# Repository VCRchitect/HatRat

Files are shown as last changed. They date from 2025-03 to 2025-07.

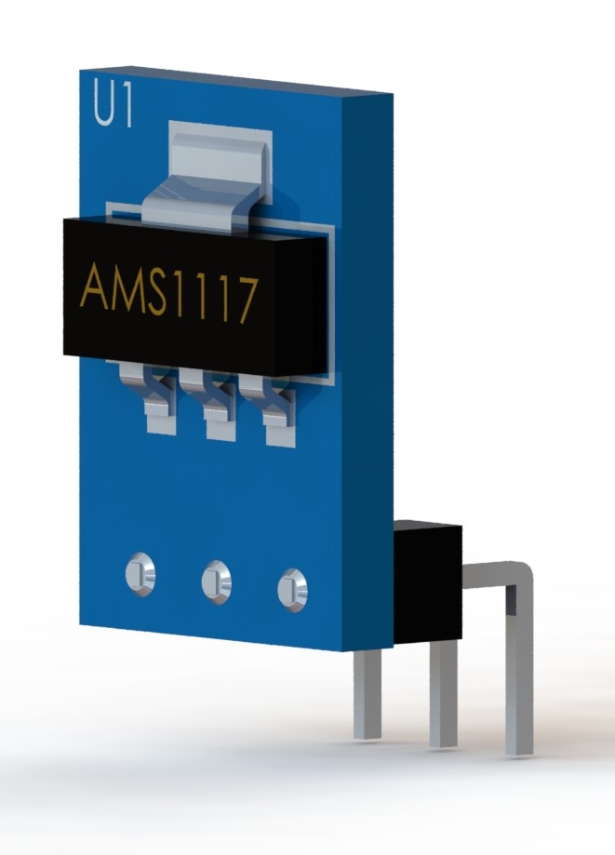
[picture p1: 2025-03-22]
KiCAD Files/Symbols and Resources/3D Models/ams1117-1.snapshot.3/AMS1117.101.jpg

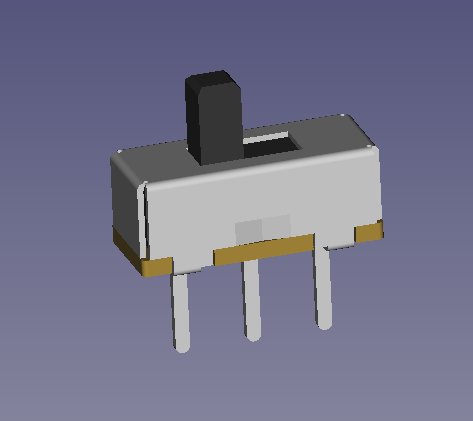
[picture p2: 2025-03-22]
KiCAD Files/Symbols and Resources/3D Models/ss12d00-1.snapshot.10/SS12D00 view 1.jpg

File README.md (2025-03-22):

HatRat, the Mouse For Your Hat!
======

This project is an attempt to make an inexpensive, easy-to-use head mouse. The shell is 3D printed and features a clip to put it on a hat, visor, or maybe even a glasses frame. 

To use the device, clip it onto something with the USB C port facing outward toward the screen. Connect a USB cable and the device will automatically turn on. Move your head up, down, left, or right to move the mouse accordingly. 

How to Use the HatRat
======
If you hold still (or even just relatively still) for 3 seconds, the mouse will enter a gesture mode:
1.  Tilt left then back to center to left-click the mouse.
2.  Tilt right then back to center to right-click the mouse.
3.  To left-click and drag, tilt to the left and keep tilted. Move your head in the direction you want to drag while keeping your head tilted. When you're done, tilt your head back to the center.
4.  To right-click and drag, tilt to the right and keep tilted. Move your head in the direction you want to drag while keeping your head tilted. When you're done, tilt your head back to the center.

If you need to reset the orientation of the mouse, look to the edge of the screen. Like, if your head is too far turned to the left, just turn all the way to the right until you're about where you want "right" to be. The same holds true for up, down, left, and right.

If you're clicking and dragging and need to drop something with precision, hold your head still for the 3 seconds to freeze the mouse in place before you tilt the opposite direction to release the click.

In the repository is the Arduino sketch, 3D print files, and KiCAD files needed to build the thing.

Bill of Materials
======
Other than the circuit board, you will need:
-	1x Arduino Pro Micro USB C
-	1x Bidirectional Logic Level Converter
-	1x AMS1117-3.3V Voltage Regulator
-	1x MPU6050 Accelerometer
-	2x Female Headers - 12 Pins - 2.54mm Pitch

You should be able to print the thing with about 25g of filament, making the entire thing cost about $15, versus the hundreds of dollars that other solutions cost.

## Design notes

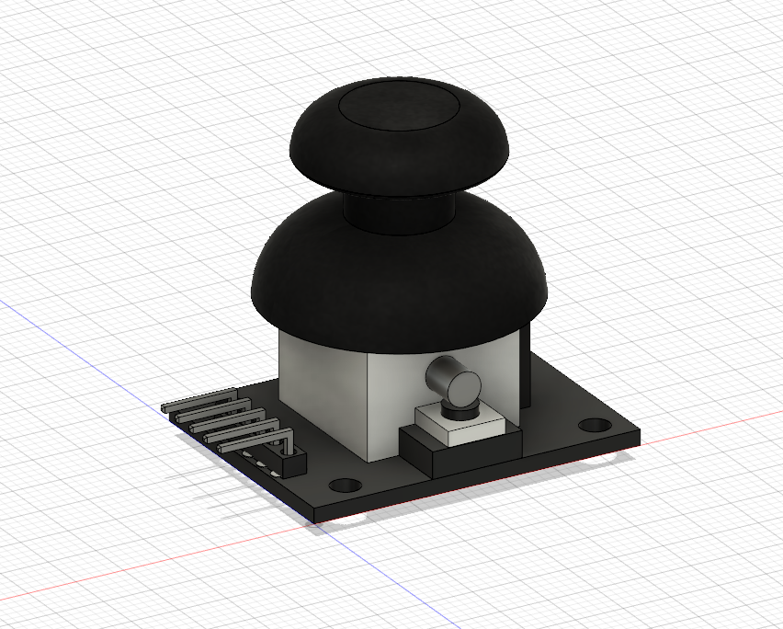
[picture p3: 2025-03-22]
KiCAD Files/Symbols and Resources/3D Models/joy-stick-4.snapshot.1/joy_stick_a2/joy_stick_2a.PNG

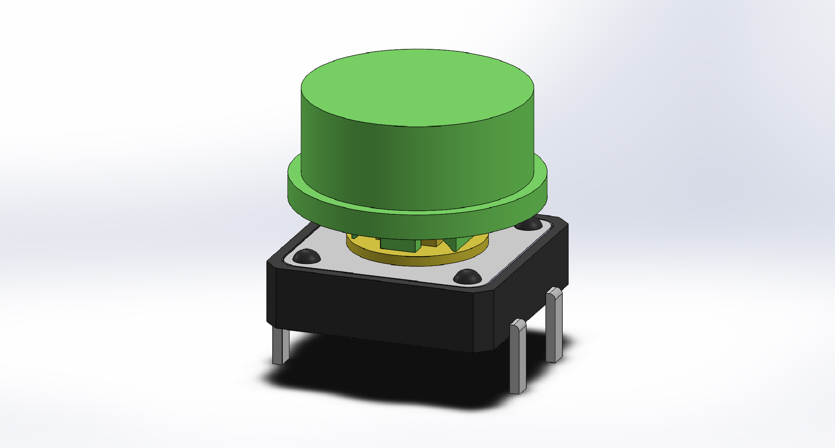
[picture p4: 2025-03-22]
KiCAD Files/Symbols and Resources/3D Models/Tactile Push Button B3F-405 12X12x7.3mm with Cap/Push Button B3F-4055 with Cap.JPG

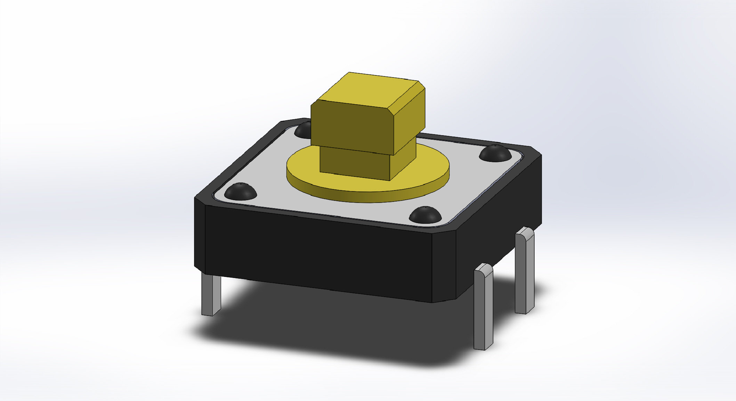
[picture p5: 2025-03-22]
KiCAD Files/Symbols and Resources/3D Models/Tactile Push Button B3F-405 12X12x7.3mm with Cap/Tactile Push Button B3F-405 12X12x7.3mm.JPG

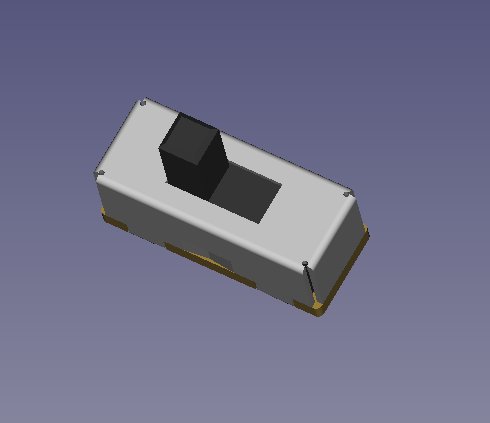
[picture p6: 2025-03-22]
KiCAD Files/Symbols and Resources/3D Models/ss12d00-1.snapshot.10/SS12D00 view 2.jpg

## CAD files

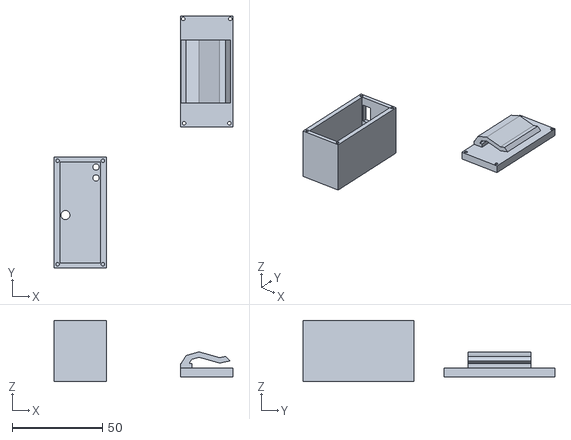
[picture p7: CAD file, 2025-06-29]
3D Print Files/HatRatV3 Shell.stl
99.0 x 139.2 x 34.0

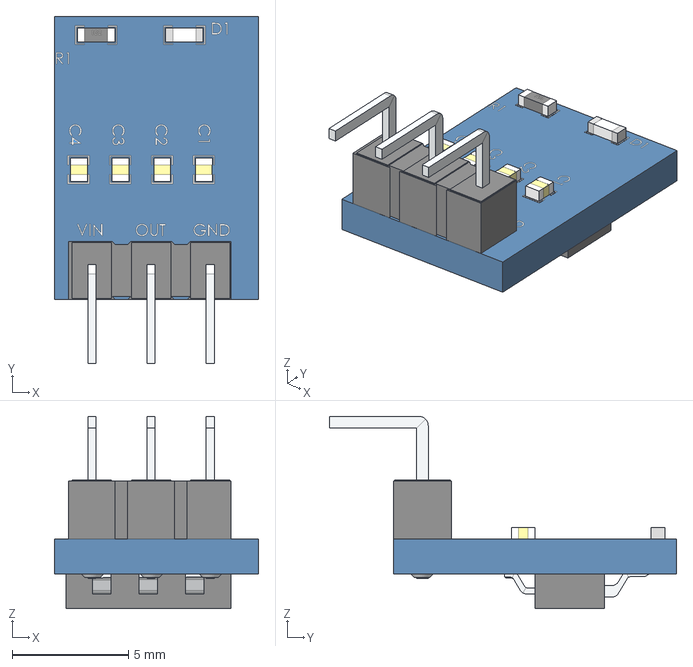
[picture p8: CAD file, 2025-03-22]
KiCAD Files/Symbols and Resources/3D Models/ams1117-1.snapshot.3/Regulador AMS1117 5V a 3.step
8.80 x 14.9 x 8.28 mm

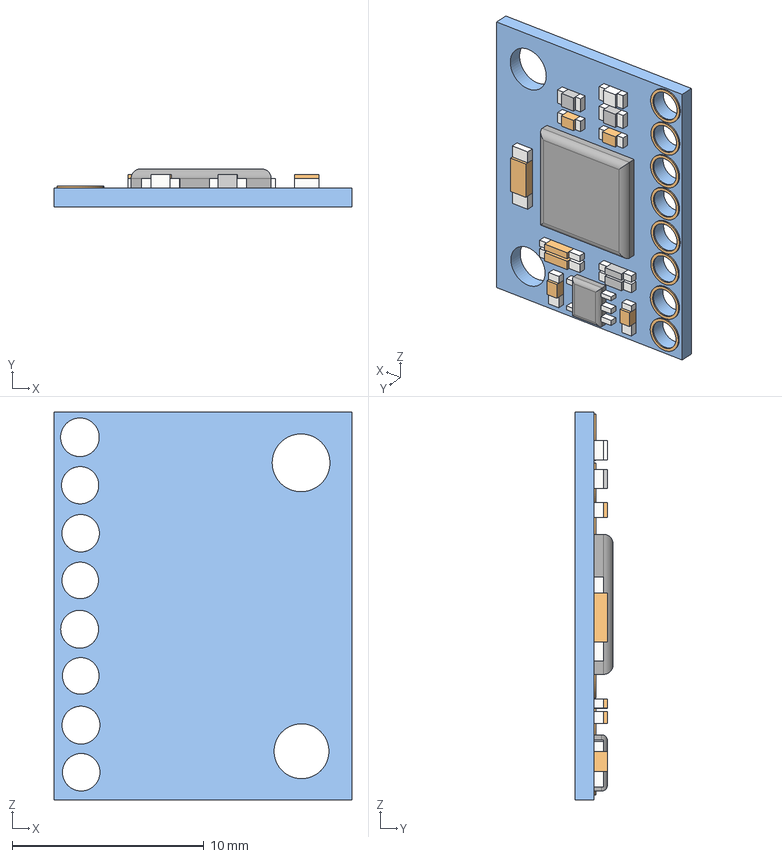
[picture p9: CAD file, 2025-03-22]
KiCAD Files/Symbols and Resources/3D Models/mpu6050-8.snapshot.1/MPU6050 v2.step
15.6 x 2.00 x 20.3 mm

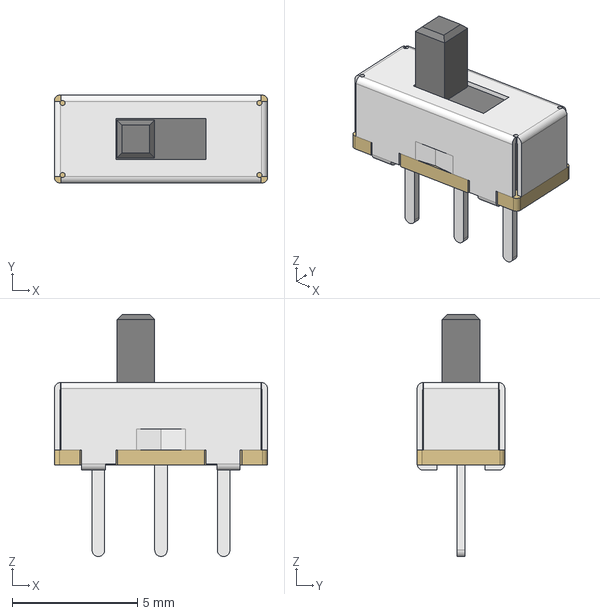
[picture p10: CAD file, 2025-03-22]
KiCAD Files/Symbols and Resources/3D Models/ss12d00-1.snapshot.10/SPDT slide switch SS12D00.step
8.50 x 3.50 x 9.66 mm

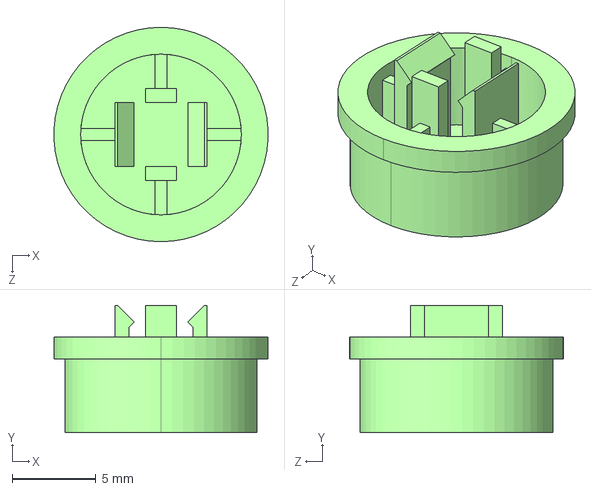
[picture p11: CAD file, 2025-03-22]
KiCAD Files/Symbols and Resources/3D Models/Tactile Push Button B3F-405 12X12x7.3mm with Cap/Tactile Button Cap for B3F-4055 12X12X7.3MM.STEP
12.8 x 7.60 x 12.8 mm

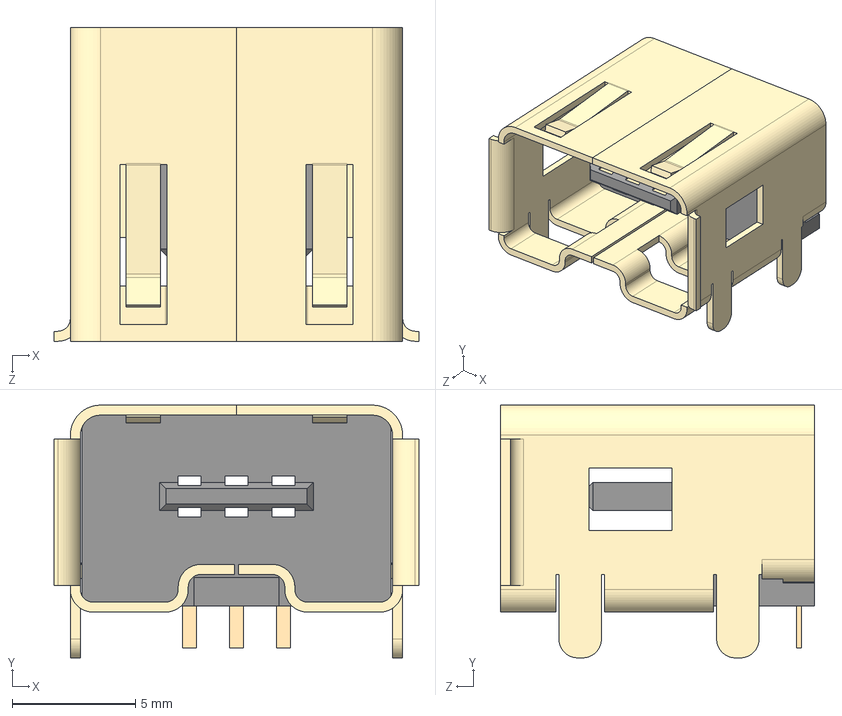
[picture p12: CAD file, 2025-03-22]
KiCAD Files/Symbols and Resources/3D Models/wiimote_f_connector.stp
14.8 x 10.2 x 12.7 mm
WII_F_TEST
INSERT

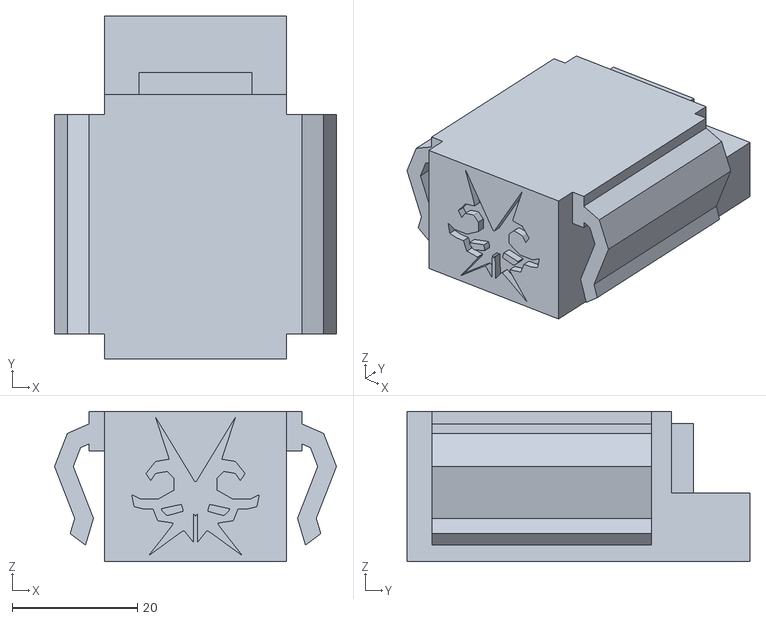
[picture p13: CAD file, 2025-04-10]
3D Print Files/SideMountHatRat Top Shell.stl
45.0 x 54.7 x 24.0

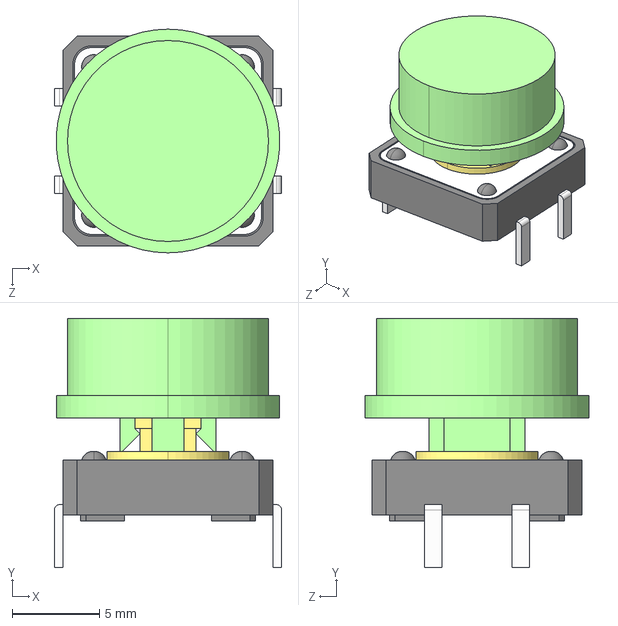
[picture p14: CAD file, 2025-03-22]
KiCAD Files/Symbols and Resources/3D Models/Tactile Push Button B3F-405 12X12x7.3mm with Cap/Push Button B3F-4055 with Cap.STEP
13.0 x 14.3 x 12.8 mm
Êíîïêà12õ12õ7,3
Tactile Button Caps for B3F-4055 12X12X7.3MM

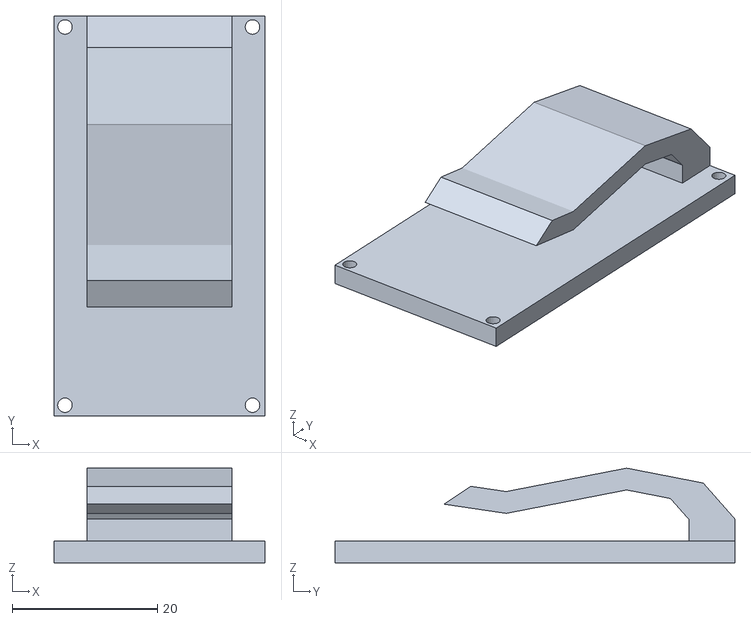
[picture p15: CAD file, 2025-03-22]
3D Print Files/HatRat Clip.stl
29.0 x 55.0 x 13.0

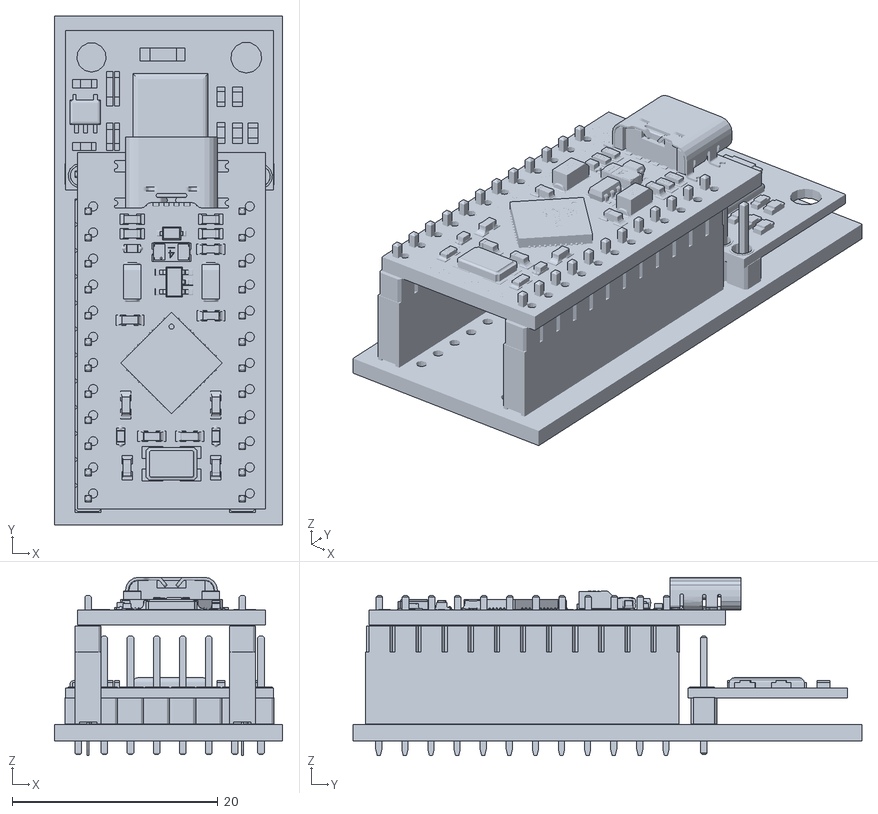
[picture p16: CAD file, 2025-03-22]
3D Print Files/HatRat PCB STL File.stl
22.2 x 49.5 x 17.4

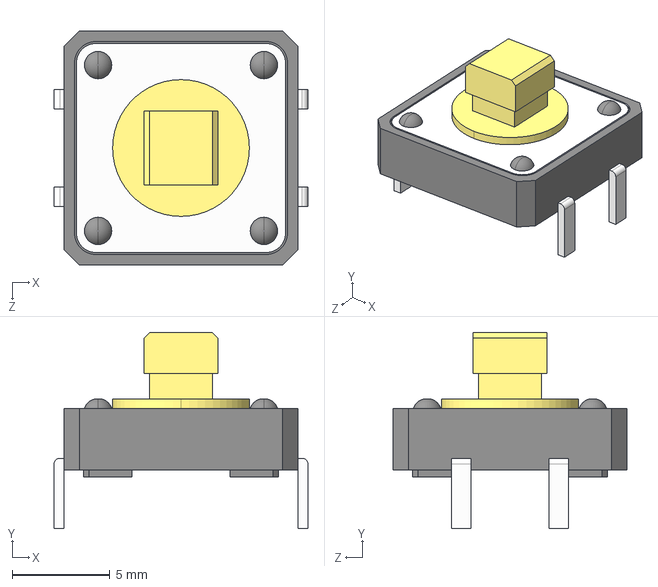
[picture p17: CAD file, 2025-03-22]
KiCAD Files/Symbols and Resources/3D Models/Tactile Push Button B3F-405 12X12x7.3mm with Cap/Tactile Push Button B3F-405 12X12x7.3mm.STEP
13.0 x 10.1 x 12.0 mm

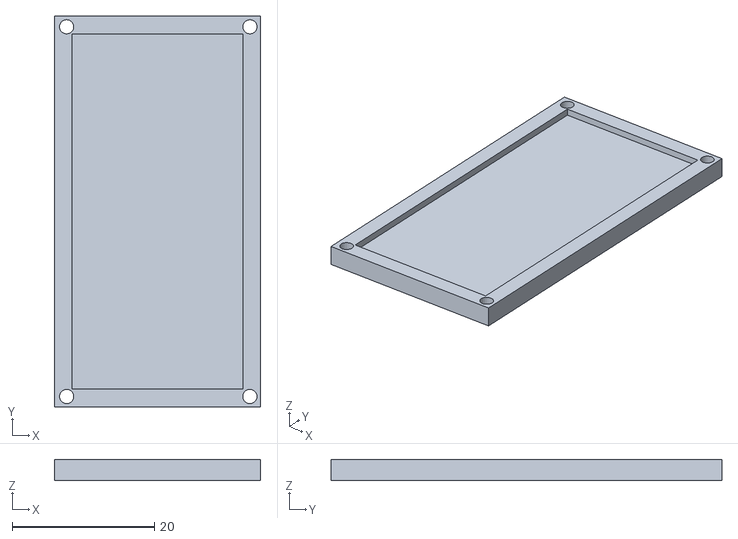
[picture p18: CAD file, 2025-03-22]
3D Print Files/HatRat Bottom.stl
29.0 x 55.0 x 3.00

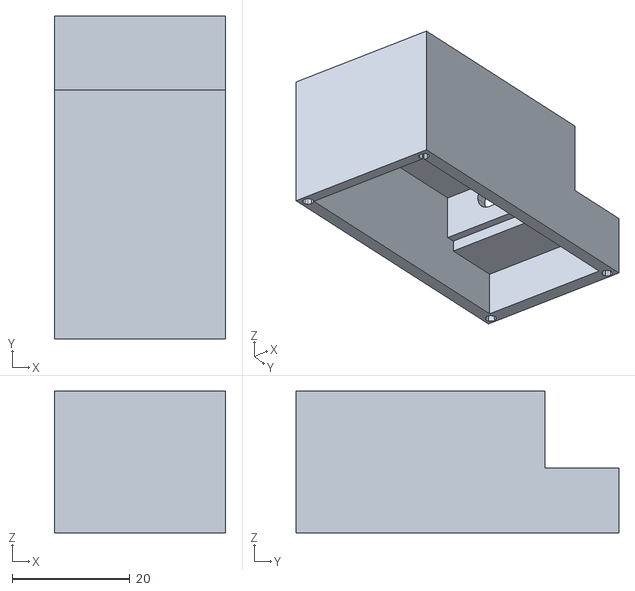
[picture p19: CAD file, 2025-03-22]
3D Print Files/HatRat Top Enclosure.stl
29.0 x 54.7 x 24.0

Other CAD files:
KiCAD Files/Symbols and Resources/3D Models/Tactile Push Button B3F-405 12X12x7.3mm with Cap/Tactile Button Caps for B3F-4055 12X12X7.3MM.SLDPRT
KiCAD Files/Symbols and Resources/3D Models/Tactile Push Button B3F-405 12X12x7.3mm with Cap/Push Button B3F-4055 with Cap.SLDASM
KiCAD Files/Symbols and Resources/3D Models/Tactile Push Button B3F-405 12X12x7.3mm with Cap/Tactile Push Button B3F-405 12X12x7.3mm.SLDPRT

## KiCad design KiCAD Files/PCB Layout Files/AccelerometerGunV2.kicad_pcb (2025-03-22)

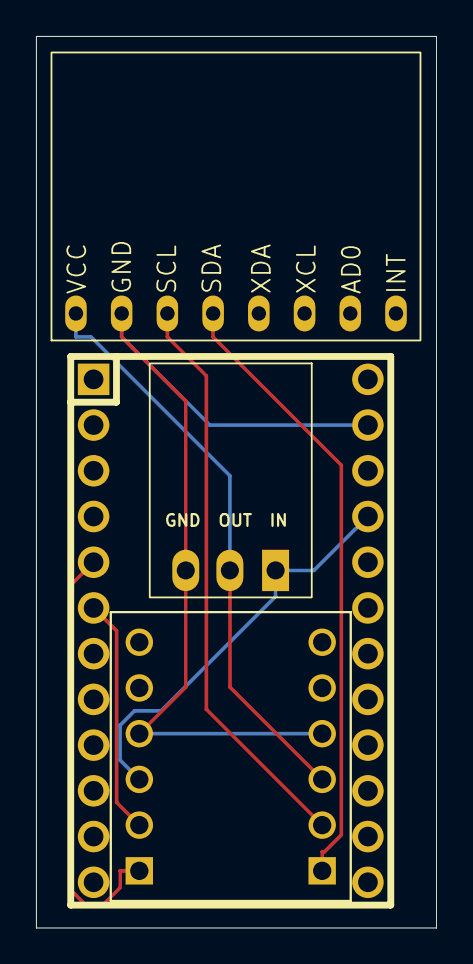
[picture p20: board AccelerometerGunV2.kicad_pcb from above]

Board: 2 copper layers, 22.2 x 49.5 mm, 4 parts (0 on the bottom side), 7 nets.

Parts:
MPU1: MPU6050 Accelerometer
U1: ProMicro; ARDUINO_PRO_MICRO
U2: 3.3v InOutGnd Voltage Regulator
U3: BOB-12009; CONV_BOB-12009

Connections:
unnamed: MPU1.2 (GND), U1.23 (GND), U2.3 (GND), U3.GND_1 (GND), U3.GND_2 (GND)
unnamed: U1.21 (VCC), U2.1 (IN), U3.HV
unnamed: MPU1.3 (SCL), U3.LV2
unnamed: MPU1.4 (SDA), U3.LV1
unnamed: MPU1.1 (VCC), U2.2 (OUT), U3.LV
unnamed: U1.6 (SCL), U3.HV2
unnamed: U1.5 (SDA), U3.HV1

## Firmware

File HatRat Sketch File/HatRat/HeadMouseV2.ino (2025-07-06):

/*********************************************************************
 *  Head-Tracker  +  Sip-&-Puff Mouse
 *  – 200 Hz Madgwick (9-DOF), non-blocking HX711 FSM,
 *    drift-free yaw, and two-position 90 ° mount switch
 *********************************************************************/

#include <Wire.h>
#include "I2Cdev.h"
#include "MPU6050.h"
#include <QMC5883LCompass.h>
#include <HX711.h>
#include <Adafruit_AHRS_Madgwick.h>
#include <Mouse.h>

/* ─── USER KNOBS ─────────────────────────────────────────── */
const float SENSITIVITY = 160.0f;       // px / deg
const float HORIZ_GAIN = -1.0f;         // flip L/R
const float PITCH_SIGN = -1.0f;         // look-down → cursor-down
const float DEADZONE_DEG = 0.03f;       // ignore < 0.03 °
const float SMOOTH_ALPHA = 0.3f;        // 0(off)…1(none)
const float FILTER_BETA = 0.11f;        // 0.10–0.15 snappy
const unsigned long LATCH_TIME = 2000;  // ms you must hold to “lock” drag


const float QUIET_DEG = 0.03f;  // hard dead-zone (º)
const float LIN_START = 0.10f;

/* Sip-&-Puff */
const long SIP_THR = -1205000;
const long PUFF_THR = 586000;
const byte HX_OVERSAMPLE = 2;
const float BASELINE_A = 0.005f;
const unsigned long CLICK_GAP = 100;  // ms
/* ─────────────────────────────────────────────────────────── */

/* Pin map */
#define PIN_UPRIGHT 0  // LOW when upright
#define PIN_ROLL90 1   // LOW when rolled left 90°
#define PIN_REZERO 2   // LOW → manual re-center
#define HX_DOUT 9
#define HX_SCK 4

/* +90 ° roll quaternion (about X) */
struct Quat {
  float w, x, y, z;
  Quat(float W = 1, float X = 0, float Y = 0, float Z = 0)
    : w(W), x(X), y(Y), z(Z) {}
  Quat conjugate() const {
    return Quat(w, -x, -y, -z);
  }
  Quat operator*(const Quat& b) const {
    return Quat(w * b.w - x * b.x - y * b.y - z * b.z,
                w * b.x + x * b.w + y * b.z - z * b.y,
                w * b.y - x * b.z + y * b.w + z * b.x,
                w * b.z + x * b.y - y * b.x + z * b.w);
  }
};
const Quat Q_ROLL90(0.7071068f, 0.7071068f, 0, 0);

/* ─── GLOBALS ────────────────────────────────────────────── */
MPU6050 mpu;
QMC5883LCompass compass;
Adafruit_Madgwick filter;
HX711 hx;

Quat qRefInv(1, 0, 0, 0);
bool haveRef = false, modeRolled = false, prevModeRolled = false;
float lastYaw = 0, lastPitch = 0, accuX = 0, accuY = 0;

/* Sip-&-puff shared vars */
long baseline = 0;
long diffFilt = 0;

/* ─── helpers ────────────────────────────────────────────── */
inline float dz(float v) {
  return (abs(v) < DEADZONE_DEG) ? 0.0f : v;
}
inline float d2(float r) {
  return r * 57.2957795f;
}
inline float w180(float a) {
  while (a > 180) a -= 360;
  while (a < -180) a += 360;
  return a;
}
inline float dAng(float a, float b) {
  return w180(a - b);
}

void zeroOrientation() {
  float w, x, y, z;
  filter.getQuaternion(&w, &x, &y, &z);
  qRefInv = Quat(w, x, y, z).conjugate();
  haveRef = true;
}

/* ─── Sip-&-Puff FSM  (non-blocking) ────────────────────── */

void sipPuff() {
  static byte sCnt = 0;
  static long sSum = 0;
  static enum { IDLE,
                SIP_HOLD,
                PUFF_HOLD } st = IDLE;
  static unsigned long pressStart = 0;
  static unsigned long lastEdge = 0;
  static bool latchedRight = false;
  static bool latchedLeft = false;
  const long SIP_LOCK_THR = SIP_THR * 2.0;    // 70 % deeper
  const long PUFF_LOCK_THR = PUFF_THR * 2.0;  // 70 % higher

  /* 1. Read HX711 -------------------------------------------------- */
  if (!hx.is_ready()) return;
  sSum += hx.read();
  if (++sCnt < HX_OVERSAMPLE) return;

  long avg = sSum / sCnt;
  sSum = 0;
  sCnt = 0;
  baseline += (long)((avg - baseline) * BASELINE_A);
  diffFilt = diffFilt * 5 / 8 + (avg - baseline) * 3 / 8;

  /* 2. State machine ---------------------------------------------- */
  unsigned long now = millis();

  switch (st) {
    /* ---------- idle: waiting for a threshold crossing ------------- */
    case IDLE:
      /* --- SIP detected (right button) --- */
      if (diffFilt < SIP_THR && now - lastEdge > CLICK_GAP) {
        if (latchedRight) {  // unlock if already latched
          Mouse.release(MOUSE_RIGHT);
          latchedRight = false;
          lastEdge = now;
        } else {
          Mouse.press(MOUSE_RIGHT);  // start a potential click
          pressStart = now;
          st = SIP_HOLD;
        }
      }
      /* --- PUFF detected (left button) --- */
      else if (diffFilt > PUFF_THR && now - lastEdge > CLICK_GAP) {
        if (latchedLeft) {
          Mouse.release(MOUSE_LEFT);
          latchedLeft = false;
          lastEdge = now;
        } else {
          Mouse.press(MOUSE_LEFT);
          pressStart = now;
          st = PUFF_HOLD;
        }
      }
      break;

      /* ---------- right button is being held ----------------- */
    case SIP_HOLD:
      /* Lock only if you are STILL below the deeper line AND time met */
      if (!latchedRight && diffFilt < SIP_LOCK_THR && now - pressStart >= LATCH_TIME) {
        latchedRight = true;  // deliberate lock
        st = IDLE;
      }
      /* Release for ordinary click */
      else if (diffFilt > SIP_THR * 0.45f) {  // raise to 45 % so it lets go sooner
        Mouse.release(MOUSE_RIGHT);
        lastEdge = now;
        st = IDLE;
      }
      break;

    /* ---------- left button is being held ------------------ */
    case PUFF_HOLD:
      if (!latchedLeft && diffFilt > PUFF_LOCK_THR && now - pressStart >= LATCH_TIME) {
        latchedLeft = true;
        st = IDLE;
      } else if (diffFilt < PUFF_THR * 0.45f) {
        Mouse.release(MOUSE_LEFT);
        lastEdge = now;
        st = IDLE;
      }
      break;
  }
}


/* ─── SETUP ──────────────────────────────────────────────── */
void setup() {
  Serial.begin(115200);
  pinMode(PIN_UPRIGHT, INPUT_PULLUP);
  pinMode(PIN_ROLL90, INPUT_PULLUP);
  pinMode(PIN_REZERO, INPUT_PULLUP);

  Wire.begin();
  Wire.setClock(400000UL);
  compass.init();
  mpu.initialize();
  mpu.setFullScaleGyroRange(MPU6050_GYRO_FS_250);
  mpu.setFullScaleAccelRange(MPU6050_ACCEL_FS_2);

  filter.begin(200);
  filter.setBeta(FILTER_BETA);

  hx.begin(HX_DOUT, HX_SCK);
  hx.set_gain(128);
  long s = 0;
  for (byte i = 0; i < 32; i++) {
    while (!hx.is_ready())
      ;
    s += hx.read();
  }
  baseline = s / 32L;

  Mouse.begin();
}

inline float softGain(float deg) {
  float absd = fabsf(deg);
  if (absd <= QUIET_DEG)  // in the absolute dead-zone
    return 0.0f;

  float sign = (deg >= 0) ? 1.0f : -1.0f;

  if (absd <= LIN_START) {                                   // cubic easing segment
    float t = (absd - QUIET_DEG) / (LIN_START - QUIET_DEG);  // 0-1
    float eased = t * t * t;                                 // cubic ramp
    return sign * eased * LIN_START;                         // ≤ LIN_START so it blends
  } else {
    return deg;  // fully linear beyond 0.15°
  }
}


/* ─── LOOP ───────────────────────────────────────────────── */
void loop() {
  /* 1. IMU + Compass → Madgwick */
  int16_t ax, ay, az, gx, gy, gz;
  mpu.getMotion6(&ax, &ay, &az, &gx, &gy, &gz);
  const float G = 1.0f / 16384.0f, D = 1.0f / 131.0f;
  compass.read();
  filter.update(gx * D, gy * D, gz * D,
                ax * G, ay * G, az * G,
                compass.getX(), compass.getY(), compass.getZ());

  if (!haveRef) zeroOrientation();

  /* 2. switch-selected roll correction */
  modeRolled = (digitalRead(PIN_ROLL90) == LOW);
  if (modeRolled != prevModeRolled) {
    zeroOrientation();
    prevModeRolled = modeRolled;
  }

  float w, x, y, z;
  filter.getQuaternion(&w, &x, &y, &z);
  Quat q = Quat(w, x, y, z) * qRefInv;
  if (modeRolled) q = q * Q_ROLL90;

  /* 3. Euler → mouse deltas */
  float yaw = d2(atan2f(2 * (q.w * q.z + q.x * q.y), 1 - 2 * (q.y * q.y + q.z * q.z)));
  float pitch = d2(asinf(2 * (q.w * q.y - q.z * q.x)));

  accuX += softGain(dAng(yaw, lastYaw)) * SENSITIVITY * HORIZ_GAIN;
  accuY += softGain(pitch - lastPitch) * SENSITIVITY * PITCH_SIGN;
  lastYaw = yaw;
  lastPitch = pitch;

  int px = int(accuX);
  accuX -= px;
  int py = int(accuY);
  accuY -= py;
  static float sX = 0, sY = 0;
  sX = sX * (1 - SMOOTH_ALPHA) + px * SMOOTH_ALPHA;
  sY = sY * (1 - SMOOTH_ALPHA) + py * SMOOTH_ALPHA;
  int mX = int(sX);
  sX -= mX;
  int mY = int(sY);
  sY -= mY;
  Mouse.move(mX, mY, 0);

  if (digitalRead(PIN_REZERO) == LOW) zeroOrientation();

  /* 4. Sip-&-Puff */
  sipPuff();
}

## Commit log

2025-03-22 Initial Commit of Files
    Here is everything you need to build a HatRat of your own!
    [AccelerometerGunV2.kicad_pcb, HatRat Bottom.stl, HatRat Clip.stl, HatRat PCB STL File.stl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]
2025-04-10 Slight Tweaks to the Code
    [SideMountHatRat Top Shell.stl]
2025-06-29 I THINK IT IS DONE
    [HatRatV2-B_Cu.gbr, HatRatV2-B_Mask.gbr, HatRatV2-B_Paste.gbr, HatRatV2-B_Silkscreen.gbr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]
